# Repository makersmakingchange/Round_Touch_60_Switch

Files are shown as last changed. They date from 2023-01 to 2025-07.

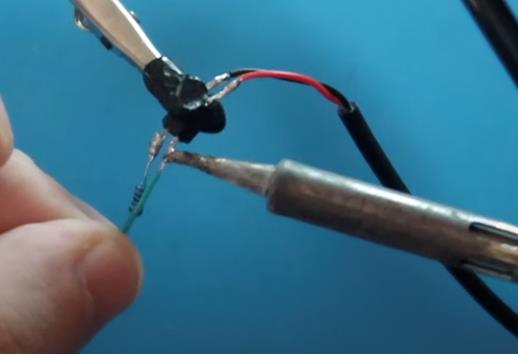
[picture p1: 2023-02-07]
Photos/Assembly_2B.jpg

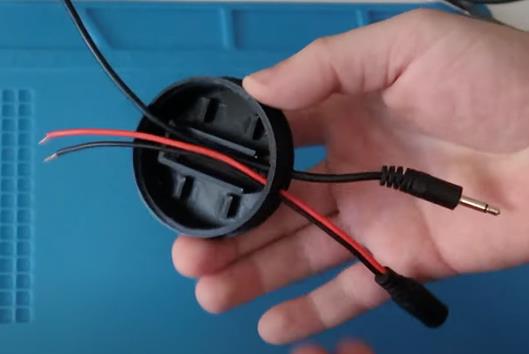
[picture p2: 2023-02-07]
Photos/Assembly_1.jpg

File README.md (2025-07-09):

<!--- Open Source Assistive Technology: GitHub Readme Template  --->

<!--- TITLE Should match the name of the GitHub repository. Choose something descriptive rather than whimsical.   --->
 # Round Touch 60 Switch

**STATUS: 2025-Jul-09. We've temporarily removed this design from the MMC OpenAT Library until some necessary design changes can be implemented.**
<!---  SUMMARY A brief summary of the project. What it does, who it is for, how much it costs.  --->
The Round Touch 60 Switch is an assistive switch that is activated by touching the top surface. This device may help users with limited hand strength and dexterity that find it challenging to activate standard mechanical switches. 

It has a standard 3.5 mm output jack, and it can be used with with standard switch adapted devices, like switch adapted toys; computer, phone, and tablet switch interfaces; and adapted gaming devices. This switch is compatible with adapted gaming controllers like the Xbox Adaptive Controller, Hori Flex Controller, and the Sony PlayStation Access Controller. 

The Round Touch 60 Switch is comprised of 3D printed parts and off-the-shelf electronics. It is based on the TTP223 Capacitive Touch boards. Assemblying the switch requires some soldering and some simple mechanical asssembly. No programming is required.

The cost of materials for a single unit is about $12 CAD, however the total cost may be quite a bit more due to several components only being available in packages of larger quantities.

<!---  PHOTO  --->
A hand activating the Round Touch 60 Switch turning on a small light.

## More info at
 - [Makers Making Change Assistive Device Library Project Page](https://www.makersmakingchange.com/s/product/round-touch-60-assistive-switch/01tJR000005KnL3YAK)

## How to Obtain a Round Touch 60 Switch
### 1. Do it Yourself (DIY) or Do it Together (DIT)
This is an open-source assistive technology, so anyone is free to build it. All of the files and instructions required to build a Round Touch 60 Switch are contained within this repository. Refer to the Maker Checklist below.

### 2. Request a build of this device
If you would like to obtain a Round Touch 60 Switch , you may submit a build request through the [MMC Library Page](https://makersmakingchange.com/project/round-touch-60-switch/). The requestor is responsible for the cost of materials and any shipping.

### 3. How to build this device for someone else
If you have the skills and equipment to build this device, and would like to donate your time to create the switch for someone who needs it, visit the [MMC Maker Wanted](https://makersmakingchange.com/maker-wanted/) section.

## Getting Started
<!---  Include an overall idea of what major steps are required to build the device.  --->

### 1. Order the Off-The-Shelf Components
The [Bill of Materials](/Documentation/Round_Touch_60_Switch_BOM.xlsx) lists all of the parts and components required to build a Round Touch 60 Switch. The electronic components may be available locally, but will probably need to be ordered online. 

### 2. Print the 3D Printable components
Print the components for the switch. All of the files and individual print files can be in the [/Build_Files/3D_Printing_Files](/Build_Files/3D_Printing_Files/) folder.

### 3. Assemble the Round Touch 60 Switch 
Reference the [assembly guide](/Documentation/Round_Touch_60_Switch_Assembly_Guide.pdf) for the tools and steps required to build each portion.

## Files
<!--- FILES This section includes all the information and files required to build and modify the device, including documentation, design files, and build files. --->

### Documentation
<!--- DOCUMENTATION --->
| Document | Version | Link |
|----------|---------|------|
| Design Rationale     | 1.0 | [Round_Touch_60_Switch_Design_Rationale](/Documentation/Round_Touch_60_Switch_Design_Rationale.pdf) |
| Maker Checklist      | 1.0 | [Round_Touch_60_Switch_Checklist](/Documentation/Round_Touch_60_Switch_Maker_Checklist.pdf) |
| Bill of Materials    | 1.0 | [Round_Touch_60_Switch_BOM](/Documentation/Round_Touch_60_Switch_BOM.xlsx) |
| Assembly Guide       | 1.0 | [Round_Touch_60_Switch_Instructions](/Documentation/Round_Touch_60_Switch_Assembly_Guide.pdf) |
| User Guide           | 1.0 | [Round_Touch_60_Switch_Quick_Guide](/Documentation/Round_Touch_60_Switch_User_Guide.pdf)           |
| Changelog            | 1.0 | [Round_Touch_60_Switch_Changelog](/Documentation/Round_Touch_60_Switch_Changelog.pdf)               |

### Design Files
<!--- DESIGN FILES If possible, include a copy of original design files to facilitate easy editing and customization. --->
Unfortunately, no design files are available for this design. If you have the skills to recreate the design to improve this project, please submit a PR or reach out to Makers Making Change below.
<!--- [CAD Files](/Design_Files/CAD) --->

### Build Files
<!--- BUILD FILES --->
 - [3D Printing Files](/Build_Files/3D_Printing_Files)

## Attribution
<!--- ATTRIBUTION Include any information related to the development of the design. This may include who identified the initial challenge, who contributed to the design --->
Original design by Jeffrey Ebin, licenced under [attribution-sharealike-4-0-international](https://creativecommons.org/licenses/by-sa/4.0/).

Documentation created by Neil Squire Society / Makers Making Change.

### Contributors
 - Jeffrey Ebin. Ebcore.
 - Eric Steinthorson. Neil Squire Society / Makers Making Change.
 - Jake McIvor. Neil Squire Society / Makers Making Change.

## License
<!--- LICENSE Choose an appropriate license. We recommend an open-source hardware compatible license. --->
Everything needed or used to design, make, test, or prepare a Round Touch 60 Switch is licensed under the CERN 2.0 Permissive license <https://ohwr.org/project/cernohl/wikis/Documents/CERN-OHL-version-2> (CERN-OHL-P).

Accompanying material such as instruction manuals, videos, and other copyrightable works that are useful but not necessary to design, make, test, or prepare the (todo: Project Title) are published under a Creative Commons Attribution-ShareAlike 4.0 license <https://creativecommons.org/licenses/by-sa/4.0/> (CC BY-SA 4.0).

----

<!-- ABOUT MMC START -->
## About Makers Making Change
[Makers Making Change Logo](https://www.makersmakingchange.com/)

Makers Making Change is a program of [Neil Squire](https://www.neilsquire.ca/), a Canadian non-profit that uses technology, knowledge, and passion to empower people with disabilities.

Makers Making Change leverages the capacity of community based Makers, Disability Professionals and Volunteers to develop and deliver affordable Open Source Assistive Technologies.

 - Website: [www.MakersMakingChange.com](https://www.makersmakingchange.com/)
 - GitHub: [makersmakingchange](https://github.com/makersmakingchange)
 - Bluesky: [@makersmakingchange.bsky.social](https://bsky.app/profile/makersmakingchange.bsky.social)
 - Instagram: [@makersmakingchange](https://www.instagram.com/makersmakingchange)
 - Facebook: [makersmakechange](https://www.facebook.com/makersmakechange)
 - LinkedIn: [Neil Squire Society](https://www.linkedin.com/company/neil-squire-society/)
 - Thingiverse: [makersmakingchange](https://www.thingiverse.com/makersmakingchange/about)
 - Printables: [MakersMakingChange](https://www.printables.com/@MakersMakingChange)

### Contact Us
For technical questions, to get involved, or to share your experience we encourage you to [visit our website](https://www.makersmakingchange.com/) or [contact us](https://www.makersmakingchange.com/s/contact).
<!-- ABOUT MMC END -->

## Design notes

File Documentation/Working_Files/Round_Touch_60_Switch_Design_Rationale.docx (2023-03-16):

# Introduction

The Round Touch 60 Switch can control 3.5 mm audio outputs like in the Xbox Adaptive Controller and other switch adapted products. This device may benefit users with limited hand dexterity and strength who find it challenging to trigger mechanical switches.

# Research

Device | Price | Link

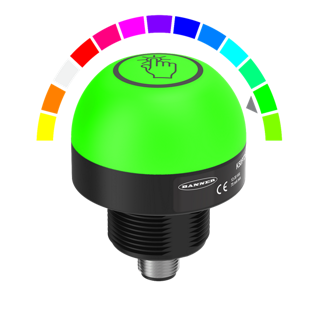
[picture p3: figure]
K50 Pro Series 50 mm Programmable Multicolor Touch Button

Capacitive Touch Button | ~$200 | Capacitive Touch Button Selection (bannerengineering.com) (https://www.bannerengineering.com/us/en/products/lighting-and-indicators/touch-buttons/capacitive.html)

# Requirements

## Goals

G01 | Allow users with limited hand dexterity/strength trigger switches

## Functional Requirements

F01 | Activate switch operated devices through a 3.5 mm mono jack
F02 | Use capacitive touch to trigger a switch

## Non-functional Requirement

NF01 | Housing should be printed without supports

## Constraints

C01 | Built with 3D printed and off the shelf components

# Detailed Design

- Design by Jeffrey Ebin and submitted to forum. (https://makersmakingchange.com/wp-admin/admin.php?page=gf_entries&view=entry&id=2&lid=10334&order=ASC&filter&paged=1&pos=6&field_id&operator)
- Capacitive touch switch with 3D printed housing.

# Opportunities for Improvement

- Battery operated.
- BOM refined for low quantity builds.

## Alternate Components

A true solid-state relay may be a more useful switch than the optocoupler (as drawn by Jeffrey Ebin, MD). While the optocoupler would be adequate for a computer input (low current), its output is polarity sensitive, and doesn't have enough current handling capacity to control many switch adapted toys. Here's a part that solves both of these issues, and for icing on the cake, is a drop-in replacement for the one in the drawing. Will cost about 5 dollars more though.
https://www.digikey.ca/en/products/detail/omron-electronics-inc-emc-div/G3VM-41AY1/5799756

© 2023 by Neil Squire / Makers Making Change This work is licensed under the CC BY SA 4.0 License: http://creativecommons.org/licenses/by-sa/4.0 Files available at https://makersmakingchange.com/project/round-touch-60-switch/ Page 1 of 2

V1.0 | January 2023 Round Touch 60 Switch Design Rationale

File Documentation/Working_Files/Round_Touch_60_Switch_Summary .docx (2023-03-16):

# Title

Round Touch 60 Switch

## Subtitle

The Round Touch 60 Switch can control 3.5mm Audio outputs like in the Xbox Adaptive Controller and other switch adapted products.

## Device Specifications

Build Time:

< 1hr

1-4 hr

5-10hr

>10hr

Cost:

$0 - $10

$11 - $25

$26 - $50

$51 - $100

$101 - $250

$250+

Stage:

Skills:

Need:

Disability:

Difficulty:

License:

Usages:

Type:

Designer:

## Device Details

The Round Touch 60 Switch can control 3.5mm Audio outputs like in the Xbox Adaptive Controller and other switch adapted products. The cost in part per unit is around $6 USD and it requires no programming.

Download the attached pdf for the parts list, wiring schematic, 3D printing files, and other project notes.

### Overview

This device may help users with limited hand strength and dexterity that find it challenging to press switches.

### Usage

To use the this device, plug in the power supply and connect the mono cable to a switch-controlled device. Simply touch the top surface to engage the switch, indicated by a red LED.

### Cost

The approximate cost of materials is 10$.

### Build Instructions

This build involves soldering electrical components and installing them into a 3D printed case. Find more information in the Assembly Guide and video tutorial.

#### Skills Required

- 3D Printing
- Soldering

#### Time Required

- 3D Printing time: 3h 26m
- Assembly Time: 30m

#### Tools

- 3D Printer
- Soldering Iron
- Hot Glue Gun
- Wire Stripper

#### 3D Printing

- Round Touch 60 Switch Housing

### Design

### Attribution

Design by Jeffrey Ebin

Documentation by Neil Squire Society / Makers Making Change

© 2023 by Neil Squire / Makers Making Change This work is licensed under the CC BY SA 4.0 License: http://creativecommons.org/licenses/by-sa/4.0 Files available at https://makersmakingchange.com/project/round-touch-60-switch/ Page 1 of 2

V1.0 | January 2023 Round Touch 60 Switch Summary

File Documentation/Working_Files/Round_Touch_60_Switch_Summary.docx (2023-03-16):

# Title

<Project Name>

## Subtitle

<Short description>

## Device Specifications

Build Time:

< 1hr

1-4 hr

5-10hr

>10hr

Cost:

$0 - $10

$11 - $25

$26 - $50

$51 - $100

$101 - $250

$250+

Stage:

Skills:

Need:

Disability:

Difficulty:

License:

Usages:

Type:

Designer:

## Device Details

### Overview

<Description, intended user>

### Usage

### Cost

### Build Instructions

<Summary of build – off-the shelf parts? Custom PCB? 3D Printing? Programming?

#### Skills Required

#### Time Required

<3D printing time>

<Assembly Time>

#### Tools

#### Components

#### 3D Printing

<If device has 3d printed components>

#### Custom PCB

#### Programming

### Design

### Attribution

<Source of idea / challenge>

<Designer>

<Any attributions for components the design is based upon>

© 2022 by <Author>. This work is licensed under the CC BY SA 4.0 License: http://creativecommons.org/licenses/by-sa/4.0 Files available at <Replace with MMC Library Link> Page 1 of 2

VX.X | <MONTH> <YEAR> <Device Name> Summary

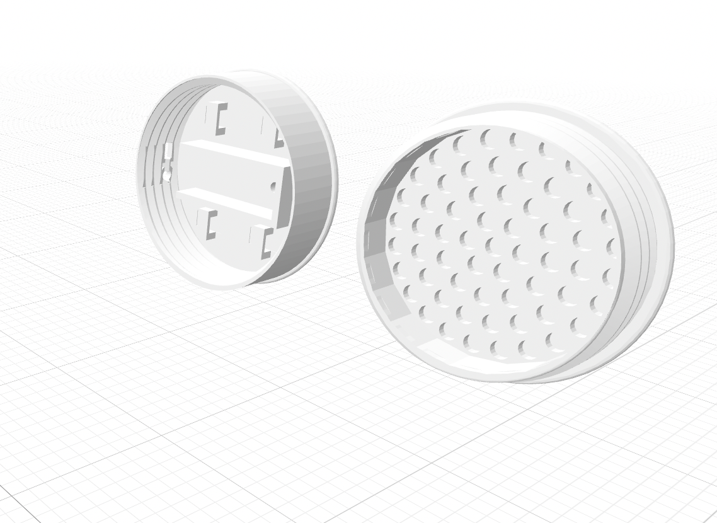
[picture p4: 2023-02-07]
Photos/Housing Model .png

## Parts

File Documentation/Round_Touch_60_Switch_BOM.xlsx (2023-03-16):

Round Touch 60 Switch |  |  |  |  |  |  |  | Unit Cost | Total Cost | Total Print time (hr) | Total filament (g)
Version: V1.0 |  | Last Updated: 2023-01-30 |  |  |  |  |  | $10.33 | $70.43 | 3.43 | 22
Commercial Parts
ID | Part Name | Part Type | QTY | QTY/PKG | $/PKG | PKG QTY | $/Unit | Extended | Total | Link
 | Touch Sensor | Electrical | 1 | 10 | $9.99 | 1 | $1.00 | $1.00 | $9.99 | Amazon.com: Aideepen 10PCS TTP223 Capacitive Touch Switch Button Self-Lock Module : Industrial & Scientific (https://www.amazon.com/gp/product/B01LWKFS7L/ref=ppx_yo_dt_b_search_asin_title?ie=UTF8&psc=1)
E6P003 | 100 Ohm Resistor | Electrical | 1 | 100 | $4.99 | 1 | $0.05 | $0.05 | $4.99 | EDGELEC 100pcs 100 ohm Resistor 1/4w (0.25 Watt) ±1% Tolerance Metal Film Fixed Resistor, Multiple Values of Resistance Optional: Amazon.com: Industrial & Scientific (https://www.amazon.com/gp/product/B07QKDSCSM/ref=ppx_yo_dt_b_search_asin_title?ie=UTF8&th=1)
PC817C | Optocoupler | Electrical | 1 | 50 | $8.99 | 1 | $0.18 | $0.18 | $8.99 | Amazon.com: WMYCONGCONG 50 PCS PC817C Optocoupler 2.54mm Pitch DIP-4 Mounting Photo Coupler for Arduino : Industrial & Scientific (https://www.amazon.com/gp/product/B0833TN6VZ/ref=ppx_yo_dt_b_search_asin_title?ie=UTF8&psc=1)
NA | DC Male Cable | Electrical | 1 | 10 | $14.99 | 1 | $1.50 | $1.50 | $14.99 | Amazon.com: DC Power Cable 12V 5A Plugs Male Female Connectors for CCTV Security Camera Pigtail Power Adapter Connectors (5.5mm x 2.1mm, 10 Pairs ) : Electronics (https://www.amazon.com/gp/product/B07C7VSRBG/ref=ppx_yo_dt_b_search_asin_title?ie=UTF8&psc=1)
US-CAB-45 | 3.5 mm Male Cable | Electrical | 1 | 10 | $14.99 | 1 | $1.50 | $1.50 | $14.99 | Amazon.com: Fancasee (10 Pack Replacement 3.5mm Male Plug to Bare Wire Open End TS 2 Pole Mono 1/8" 3.5mm Plug Jack Connector Audio Cable Repair : Electronics (https://www.amazon.com/gp/product/B082VVPTN6/ref=ppx_yo_dt_b_search_asin_title?ie=UTF8&psc=1)
 | Power Supply | Electrical | 1 | 2 | $10.99 | 1 | $5.50 | $5.50 | $10.99 | Amazon.com: Facmogu 2 Pack DC 5V 2A Power Adapter, AC 100-240V to DC 5V 2A 10W Power Supply Transformers, 5.5 x 2.5mm DC Jack Also Compatible with 5.5x2.1mm Socket : Electronics (https://www.amazon.com/gp/product/B08722QC75/ref=ppx_yo_dt_b_search_asin_title?ie=UTF8&th=1)
 | Zip Ties | Mechanical | 1 | 100 | $5.49 | 1 | $0.05 | $0.05 | $5.49 | Amazon.com: TR Industrial Multi-Purpose UV Resistant Black Cable Ties, 4 inches, 100 Pack : Everything Else (https://www.amazon.com/TR-Industrial-TR88301-Multi-Purpose-Cable/dp/B01018DB2E)
3D Printed Parts ESTIMATED PRICING USING 1KG ROLL COST: |  | $25.00
ID | Part | Material | QTY | Mass (g) / Unit | Time / Unit |  | Print Time (Min) | Estimated Price |  | Link
 | Case | PLA | 1 | 22 | 206 |  | 206 | $0.55 |  | Touch Switch by Ebcore - Thingiverse (https://www.thingiverse.com/thing:5628657)
 |  |  |  |  |  |  |  | $0.00
Custom Printed Circuit Board (PCB)
ID | Part |  | QTY
 | Not required
Tools for Assembly
 | Soldering Iron / Solder
 | Hot Glue Gun / Hot Glue
Alternatives (if there are other sources for some parts link them below)
ID | Part and description | Part Type |  | QTY/PKG | $/PKG |  | Link
 | Touch Sensor | Electrical |  | 20 | $12.99 |  | https://www.amazon.ca/dp/B01D1D0FLG?_encoding=UTF8&psc=1&ref_=cm_sw_r_cp_ud_dp_QGGJ142876K1KE94305V
NFR25H0001000JR500 | 100 Ohm Resistor | Electrical |  | 1 | $0.62 |  | NFR25H0001000JR500 Vishay / BC Components | Mouser Canada (https://www.mouser.ca/ProductDetail/Vishay-BC-Components/NFR25H0001000JR500?qs=H30XFsNYD%2FEWxhcyLyBucg%3D%3D)
PS2565-1-V-A | Optocoupler | Electrical |  | 1 | $2.01 |  | PS2565-1-V-A Renesas Electronics | Mouser Canada (https://www.mouser.ca/ProductDetail/Renesas-Electronics/PS2565-1-V-A?qs=qSfuJ%252Bfl%2Fd4lKIOVtP5dvA%3D%3D)
 | DC Male Cable | Electrical |  | 10 | $14.99 |  | https://www.amazon.ca/dp/B0B429K3VN?ref_=cm_sw_r_cp_ud_dp_Z8F8DY6MMHFM11J52DES
 | DC Cable Male to Female - cut in half | Electrical |  | 1 | $4.34 |  | https://www.digikey.ca/en/products/detail/adafruit-industries-llc/327/6827037
 | 3.5 mm Male Cable |  |  | 4 | $13.99 |  | https://www.amazon.ca/dp/B0B3MN43C5?_encoding=UTF8&psc=1&ref_=cm_sw_r_cp_ud_dp_5JVVVC76WPC272491VS9
 | Power Supply | Electrical |  | 2 | $17.99 |  | https://www.amazon.ca/dp/B08722QC75?_encoding=UTF8&psc=1&ref_=cm_sw_r_cp_ud_dp_K4SNYG36DGHQZTGWG1EY

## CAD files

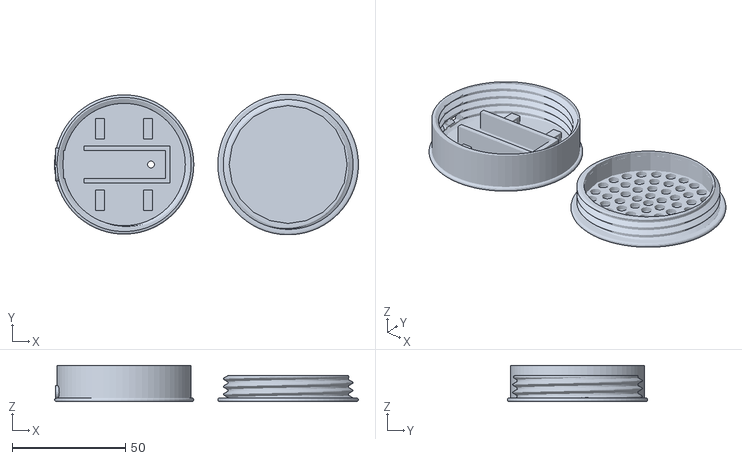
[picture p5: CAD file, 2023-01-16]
Build_Files/3D_Printing_Files/Round_Touch_60_Switch_Housing.stl
134.0 x 61.9 x 16.1

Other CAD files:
Design_Files/CAD_Files/OpenAT_Placard.f3d

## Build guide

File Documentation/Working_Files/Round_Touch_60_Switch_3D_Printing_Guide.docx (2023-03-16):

# 3D Printing Summary

Metrics | Configuration 1
Total Print Time (min) | 206
Total Number of Components | 2
Typical Total Mass (g) | 22
Typical Number of Print Setups | 1

# 3D Printing Settings

Print File Name | Qty | Total Print Time (hr:min) | Mass (g) | Infill (%) | Support (Y/N) | Layer Height/ Nozzle Diameter(mm) | Notes (orientation, special settings, etc.)
Round_Touch_Switch_60_Housing.stl | 1 | 3:26 | 22 | 20 | N | 0.2/0.4 | Print in orientation given in STL

# Customization Options

Users may request their choice of print colour.

# Post-Processing

Inspect that all surfaces are smooth, and holes are free of filament.

# Examples of Quality Prints

Photos of Housing Lid

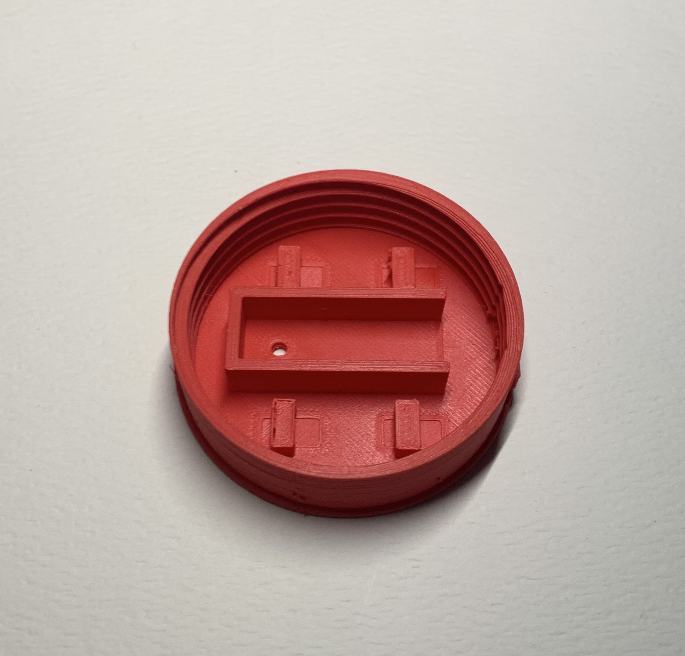
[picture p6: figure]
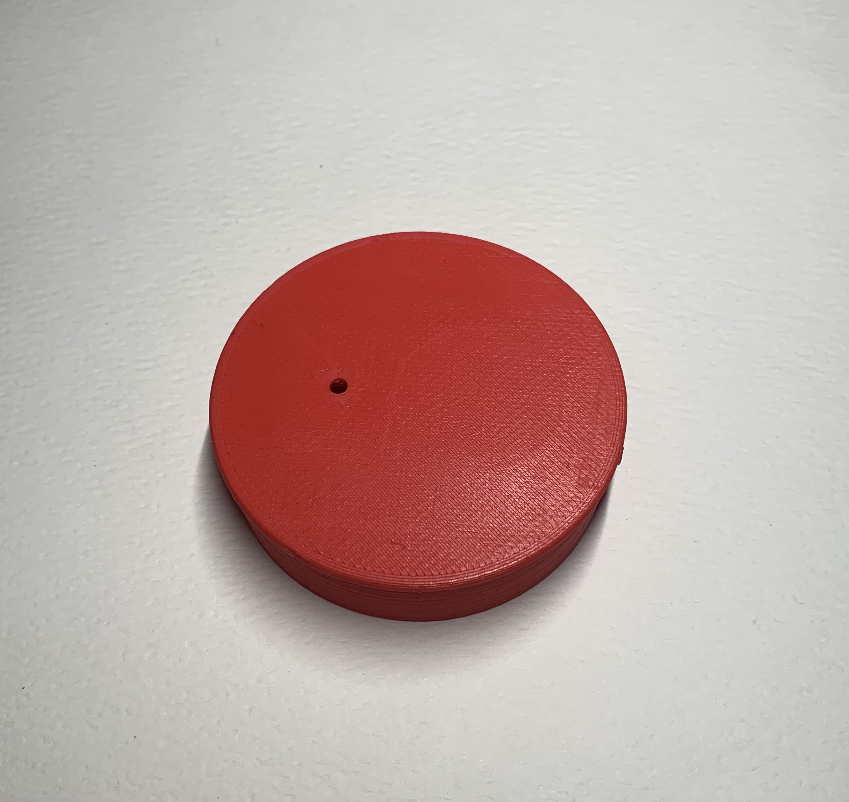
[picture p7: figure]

Photos of Housing Base

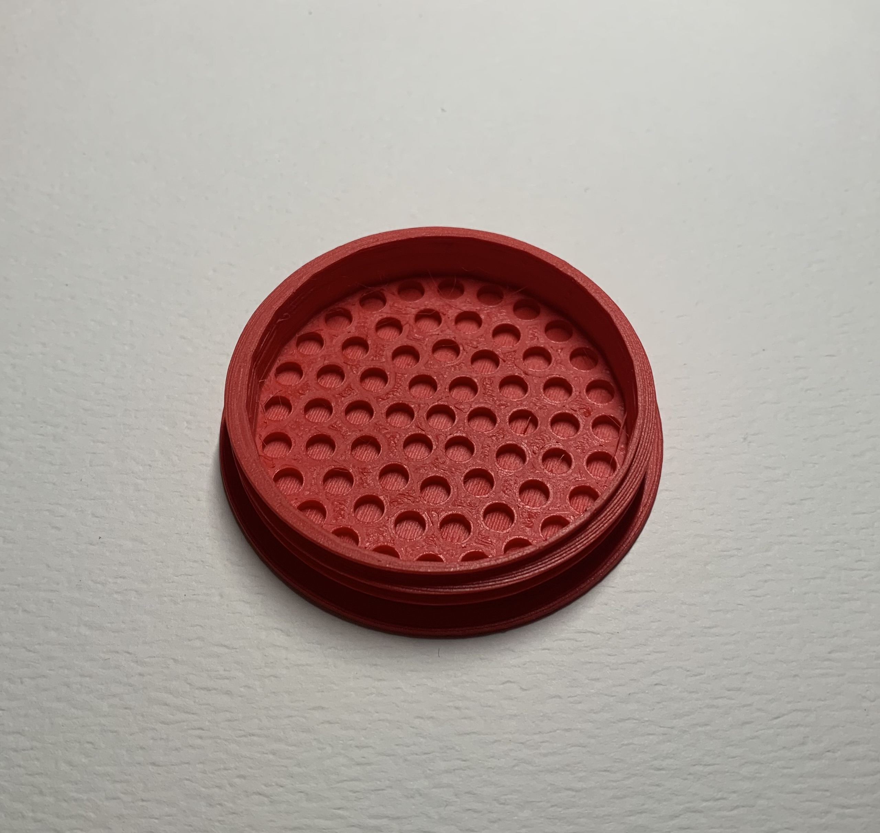
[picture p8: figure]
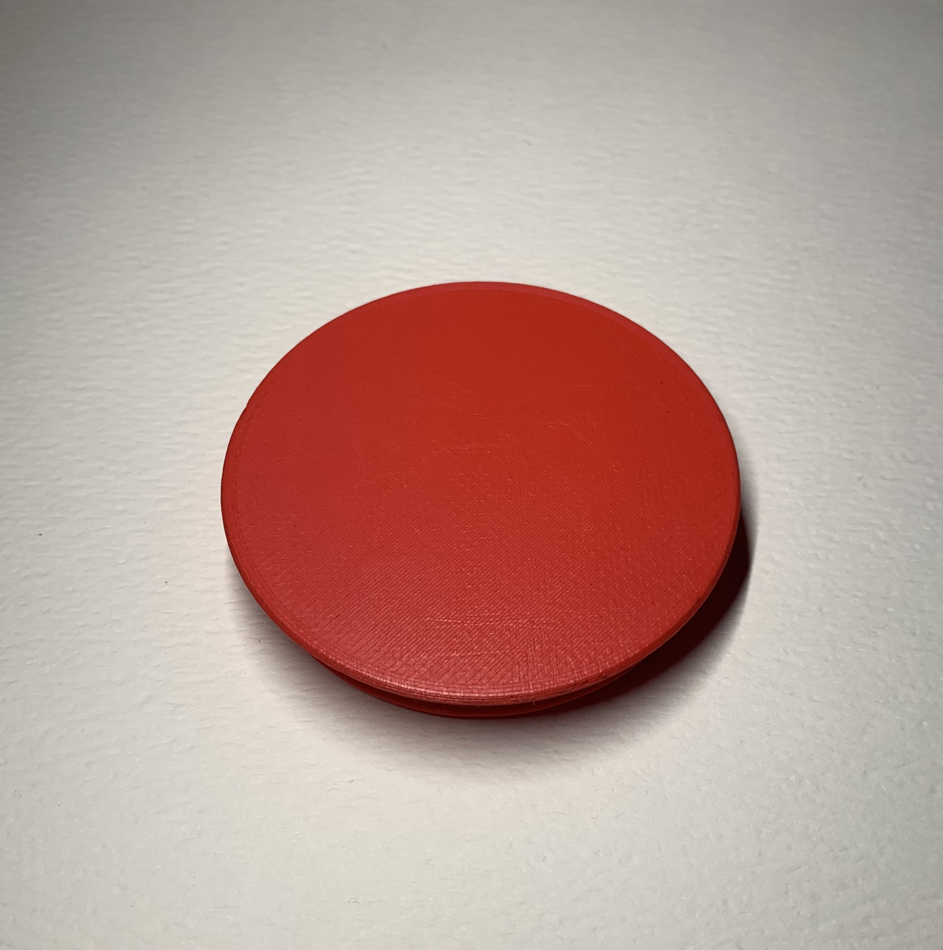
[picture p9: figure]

© 2023 by Neil Squire / Makers Making Change This work is licensed under the CC BY SA 4.0 License: http://creativecommons.org/licenses/by-sa/4.0 Files available at https://makersmakingchange.com/project/round-touch-60-switch/ Page 1 of 2

V1.0 | January 2023 Round Touch 60 Switch 3D Printing Guide

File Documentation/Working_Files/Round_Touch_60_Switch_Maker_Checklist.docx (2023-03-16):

# Maker To Do List

- Read through the Assembly Guide to become familiar with required components, tools, supplies, and safety gear and overall assembly steps.
- Talk to User about customization options (e.g., color, any special requests, etc.)
- Order hardware components
- Gather tools, supplies, and safety equipment.
- Assemble the device
- Test device
- Print “User Quick Guide”

# Items to Give to User

- Assembled, tested device
- “User Quick Guide”

© 2023 by Neil Squire / Makers Making Change This work is licensed under the CC BY SA 4.0 License: http://creativecommons.org/licenses/by-sa/4.0 Files available at https://makersmakingchange.com/project/round-touch-60-switch/ Page 1 of 2

V1.0 | January 2023 Round Touch 60 Switch Maker Checklist

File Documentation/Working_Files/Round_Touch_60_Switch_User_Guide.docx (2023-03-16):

## Introduction

The Round Touch 60 Switch can control 3.5 mm audio outputs like in the Xbox Adaptive Controller and other switch adapted products. This device may benefit users with limited hand dexterity and strength who find it challenging to trigger mechanical switches.

## Features

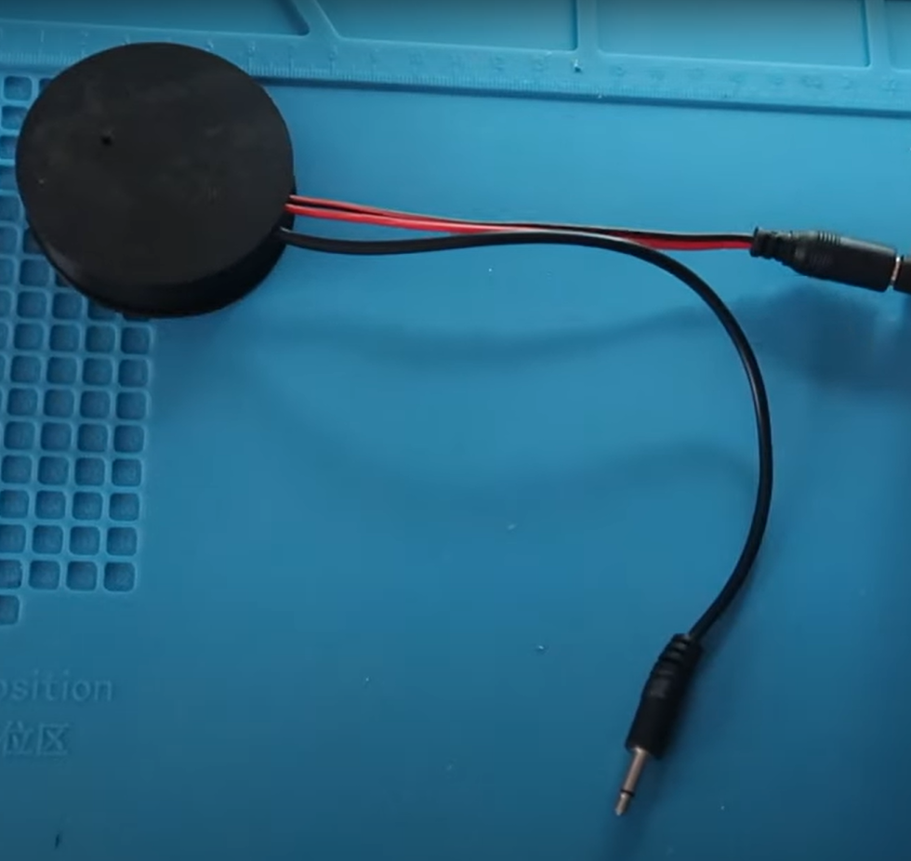
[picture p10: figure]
A black 3D printed Touch Switch with power and mono cables coming out of the case.

3.5 mm Mono Cable Output

Touch Sensor

Power Input

## Usage

To use this device, plug in the power supply and connect the mono cable to a switch-controlled device. Simply touch the top surface to engage the switch, indicated by a red LED.

## Compatibility

This device can trigger any device that requires a 3.5 mm momentary switch.

## Specifications

Diameter | Height | Power Input | Switch Output
6.1 cm | 1.8 cm | 5V 2A | 3.5 mm mono cable

## Cleaning

Unplug the device and wipe down with a damp cloth or cleaning wipes. Do not get the internal electronics wet.

© 2023 by Neil Squire / Makers Making Change This work is licensed under the CC BY SA 4.0 License: http://creativecommons.org/licenses/by-sa/4.0 Files available at https://makersmakingchange.com/project/round-touch-60-switch/ Page 1 of 2

V1.0 | January 2023 Round Touch 60 Switch user Quick Guide

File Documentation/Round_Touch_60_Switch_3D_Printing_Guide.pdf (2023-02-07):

V1.0 | January 2023

## Round Touch 60 Switch

## 3D PRINTING GUIDE

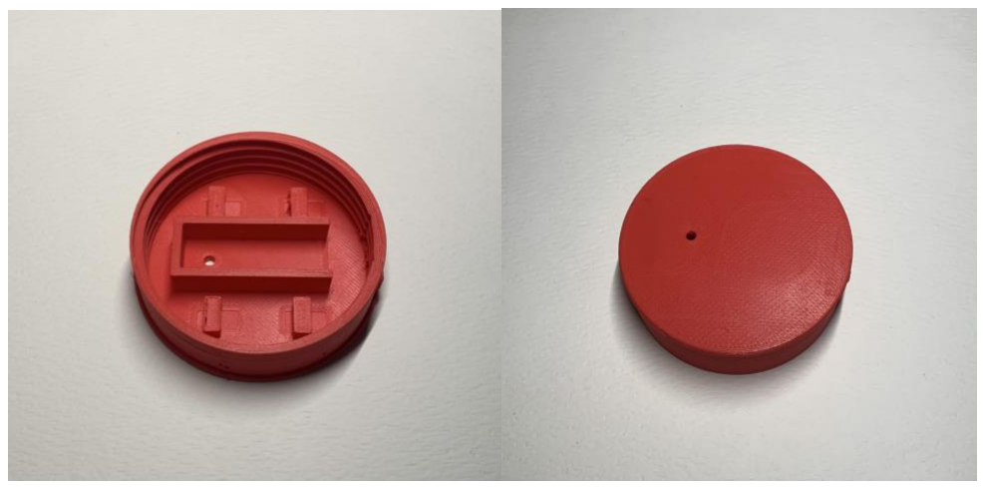
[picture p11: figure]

© 2023 by Neil Squire / Makers Making Change (https://www.neilsquire.ca/) This work is licensed under the CC BY SA 4.0 License: http://creativecommons.org/licenses/by-sa/4.0 Files available at https://makersmakingchange.com/project/round-touch-60-switch/

### 3D Printing Summary

Metrics | Configuration 1
Total Print Time (min) | 206
Total Number of Components | 2
Typical Total Mass (g) | 22
Typical Number of Print Setups | 1

### 3D Printing Settings

Print File Name | Qt y | Total Print Time (hr:min) | Mass (g) | Infill (%) | Support (Y/N) | Layer Height/ Nozzle Diameter(mm) | Notes (orientation, special settings, etc.)
Round_Touch_Switch _60_Housing.stl | 1 | 3:26 | 22 | 20 | N | 0.2/0.4 | Print in orientation given in STL

### Customization Options

Users may request their choice of print colour.

### Post-Processing

Inspect that all surfaces are smooth, and holes are free of filament.

### Examples of Quality Prints

Photos of Housing Lid

V1.0 | January 2023

## Round Touch 60 Switch

## 3D PRINTING GUIDE

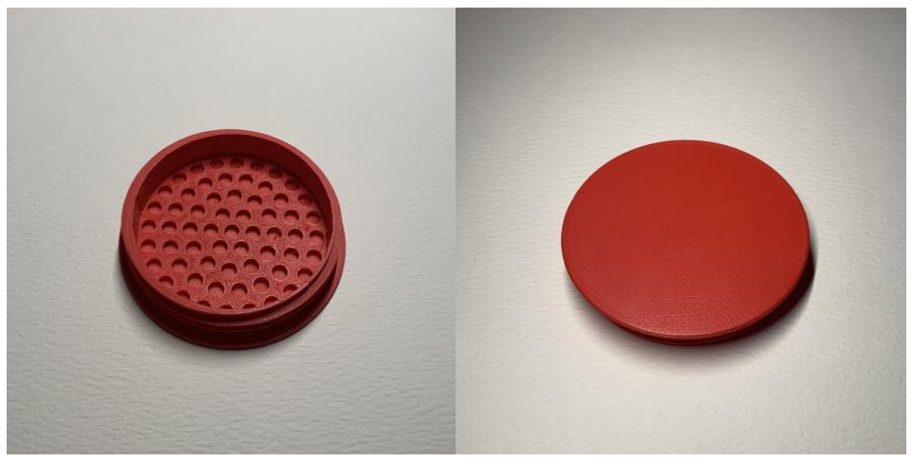
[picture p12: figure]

© 2023 by Neil Squire / Makers Making Change (https://www.neilsquire.ca/) This work is licensed under the CC BY SA 4.0 License: http://creativecommons.org/licenses/by-sa/4.0 Files available at https://makersmakingchange.com/project/round-touch-60-switch/

Photos of Housing Base

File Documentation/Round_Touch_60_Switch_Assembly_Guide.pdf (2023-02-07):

V1.0 | January 2023

# Round Touch 60 Switch

# ASSEMBLY GUIDE

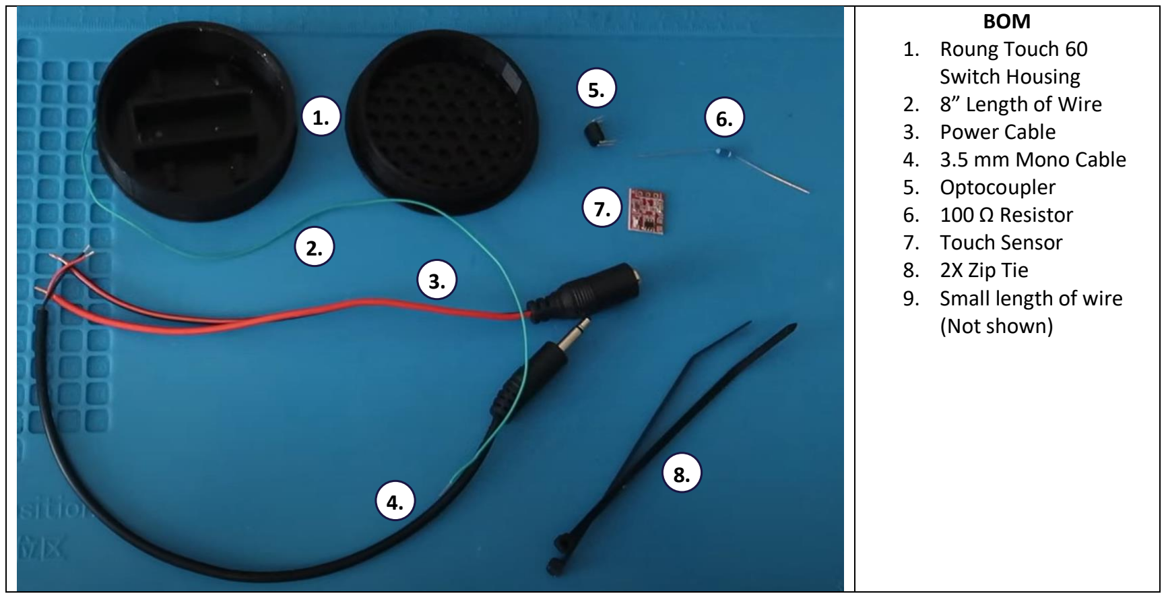
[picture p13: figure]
BOM 1. Roung Touch 60 Switch Housing 2. 8” Length of Wire 3. Power Cable 4. 3.5 mm Mono Cable 5. Optocoupler 6. 100 Ω Resistor 7. Touch Sensor 8. 2X Zip Tie 9. Small length of wire (Not shown)

© 2023 by Neil Squire / Makers Making Change (https://www.neilsquire.ca/) This work is licensed under the CC BY SA 4.0 License: http://creativecommons.org/licenses/by-sa/4.0 Files available at https://makersmakingchange.com/project/round-touch-60-switch/

# Required Components

# Required Tools

## - Soldering Iron - Solder - Wire Strippers - Hot Glue Gun - Hot Glue

# Required Personal Protective Equipment (PPE)

## - Safety Glasses - Fume Extractor or a well-ventilated space

# ASSEMBLY GUIDE

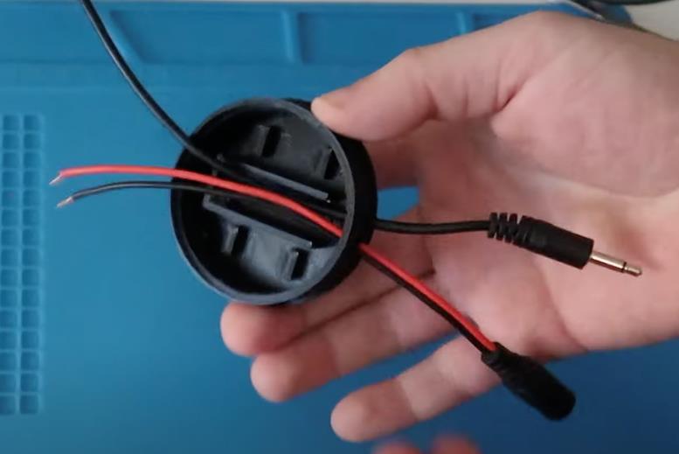
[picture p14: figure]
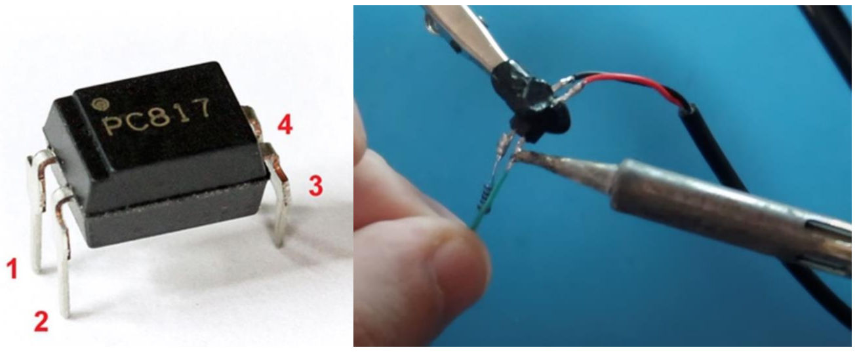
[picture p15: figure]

© 2023 by Neil Squire / Makers Making Change (https://www.neilsquire.ca/)

# Assembly Instructions

## Step 1

Place the two wires into the case.

## Step 2

## Solder the optocoupler connections:

## 1 - 100 Ω resistor 2 - Small length of wire 3 - 3.5mm mono cable 4 - 3.5mm mono cable

## Note: Pins 3 and 4 on the optocoupler are soldered to the red and black wires of the mono

cable. The order of black and red wires does not matter as long as they are on those pins.

# ASSEMBLY GUIDE

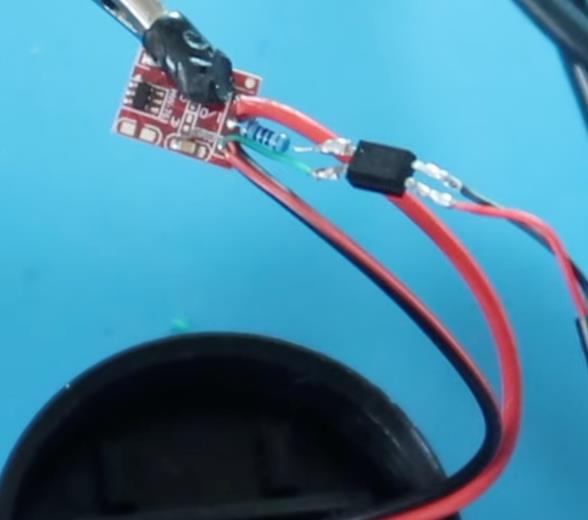
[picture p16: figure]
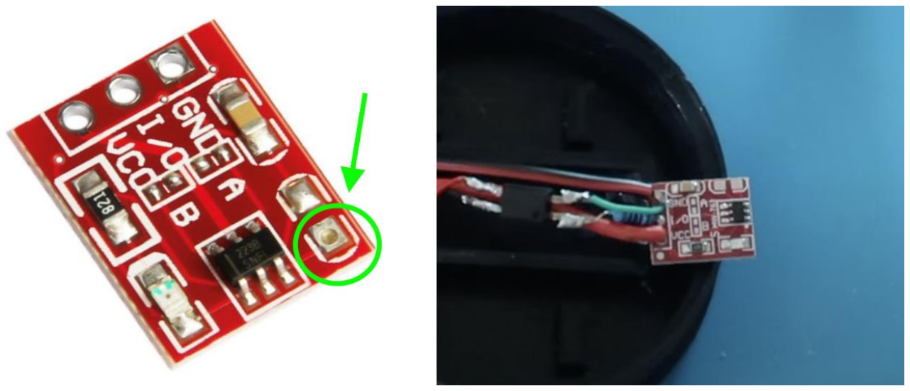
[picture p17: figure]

© 2023 by Neil Squire / Makers Making Change (https://www.neilsquire.ca/)

## Step 3

## Solder the Touch Sensor connections: Solder the red power cable to the VCC pin, the 100 Ω

resistor to the I/O pin, the ground power cable and short wire (from pin 2 on the optocoupler) to the GND pin on the touch sensor.

## Step 4

Solder the 8” length of wire to the top right of the touch sensor, seen in the green circle.

# ASSEMBLY GUIDE

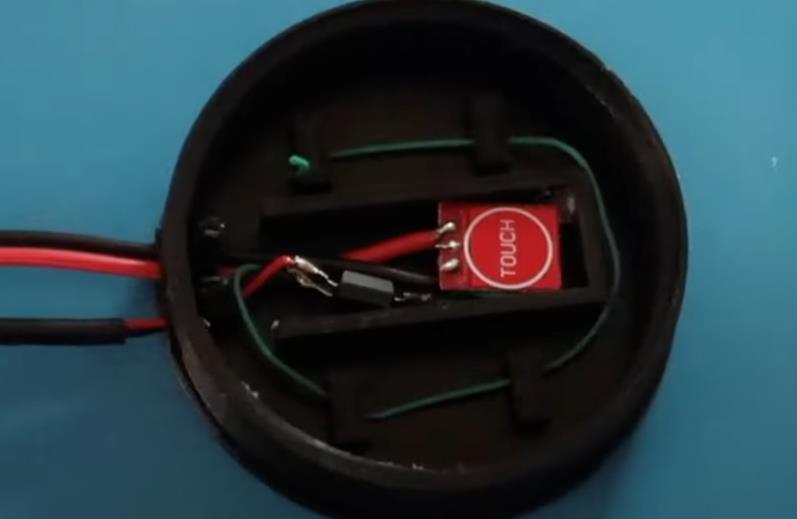
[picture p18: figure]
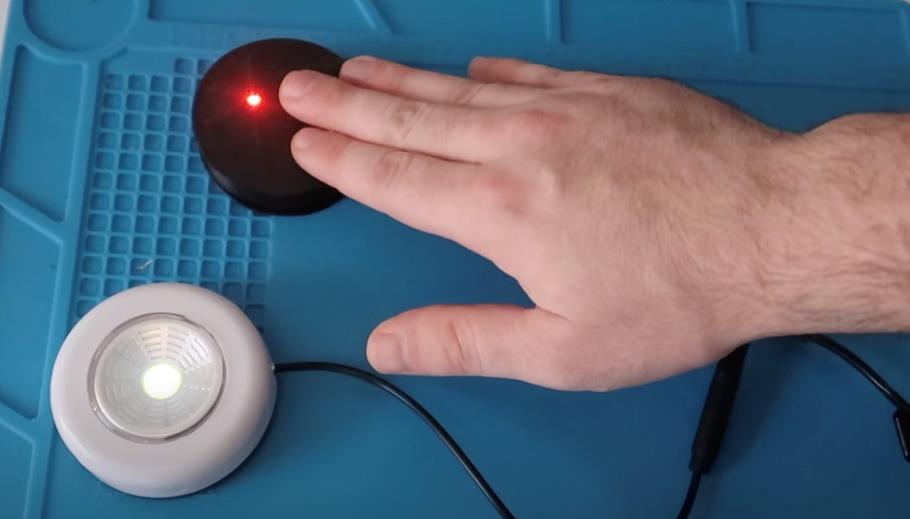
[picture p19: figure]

© 2023 by Neil Squire / Makers Making Change (https://www.neilsquire.ca/)

## Step 5

Place all the components into the case and run the wire through the tabs as shown below. Use hot glue to help secure all the electronics and attach the zip ties around the power cable and mono cable within the case to secure them if pulled.

## Step 6

## Screw on the top of the case and plug the power cable into the 5V 2A power supply to

complete the build. If the device does not work, check all the electronic connections.

For more detailed instructions, watch the Touch Twitch build tutorial: Touch Switch Tutorial - YouTube (https://www.youtube.com/watch?v=Iro8C4j6y7s)

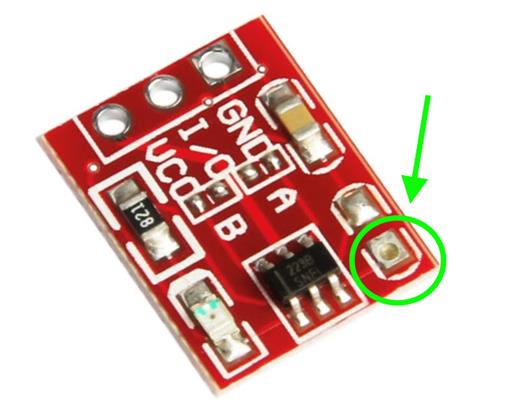
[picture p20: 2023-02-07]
Photos/Assembly_4B.jpg

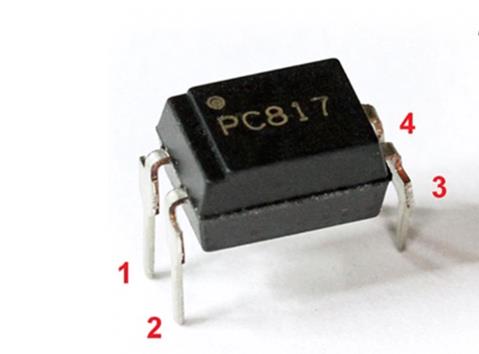
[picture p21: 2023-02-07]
Photos/Assembly_2A.jpg

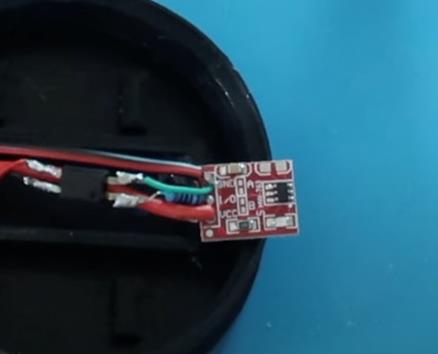
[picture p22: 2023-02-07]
Photos/Assembly_4A.jpg

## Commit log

2023-01-16 Files Added
    [OpenAT_Placard.stl, Touch_Switch_Housing.stl]
2023-03-16 Files Updated
    [DeviceName_BOM.xlsx, Round_Touch_60_Switch_BOM.xlsx]
